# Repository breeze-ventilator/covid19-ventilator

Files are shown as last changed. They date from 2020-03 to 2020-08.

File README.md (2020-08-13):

#  Breeze Ventilator
Welcome to our open-source, low-cost ventilator design! We are a group of students, physicians and engineers who worked on the design to help alleviate the critical need for ventilators during the COVID-19 pandemic.

Here is a [video](https://youtu.be/5ufh_80dSsk) with an overview of our design.

<p align="center">
  <a href="https://youtu.be/5ufh_80dSsk" target="_blank">
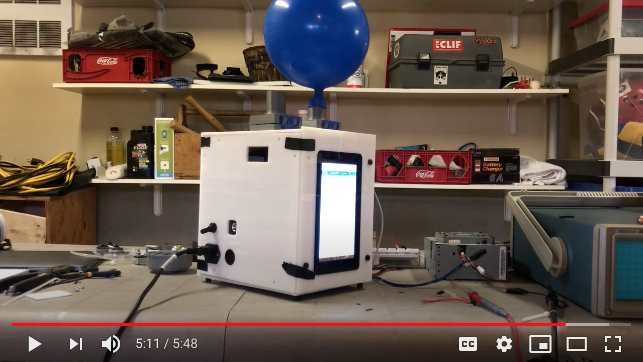
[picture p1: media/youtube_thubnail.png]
Play Introduction Video
    
  </a>
</p>

You can also check out our [in depth design video](https://youtu.be/dRpsoaCI0QA) and [public announcement video](https://youtu.be/4-jjhEgUjkQ).

## Operational Diagram
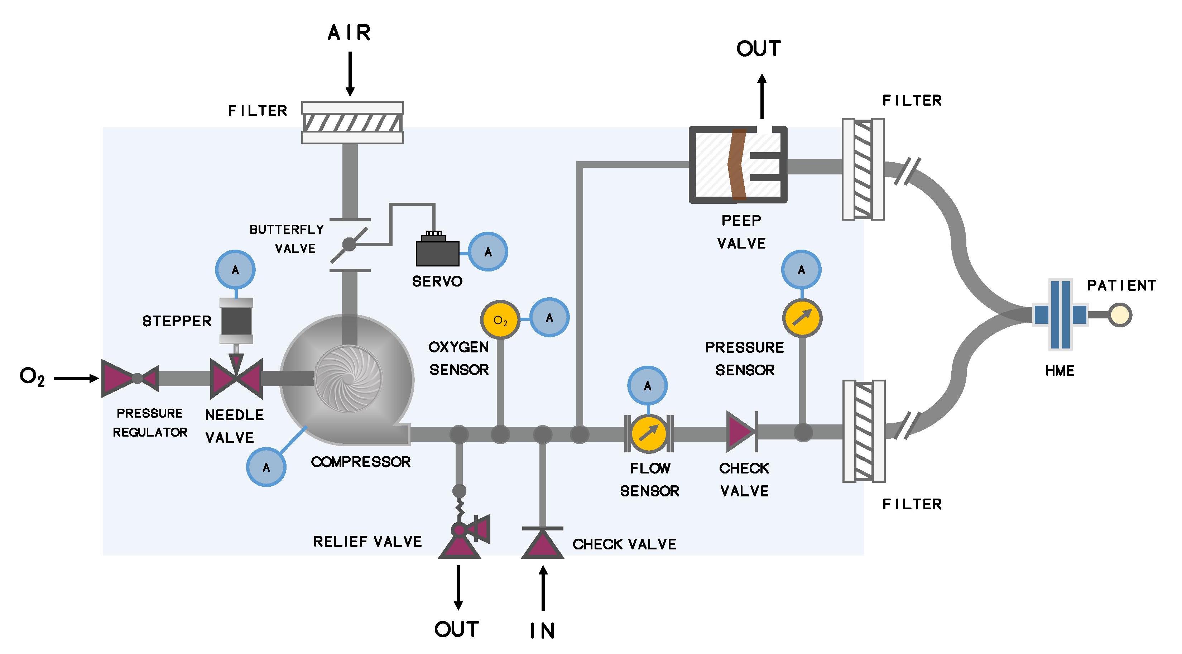
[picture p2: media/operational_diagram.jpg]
operational diagram


## Folder Structure
**Mechanical:** Everything you need to construct the device including the bill of materials and the CAD files.

**Software:** Breeze ventilator code including code for both the interface (running on the Raspberry Pi 4) and the firmware (running on the Arduino Mega).

**Electronics:** PCBs and the circuit diagrams.

**Documentation:** Documentation for operating the device including the User Guide and the Assembly guide, which will help you set-up and run your device smoothly.

## Conclusion

The Breeze Ventilator was built during a design sprint and is not ready to be safely used as a functioning ventilator. Nevertheless, we hope that you will find inspiration from our design and that it will help you with your projects! 

If you have any comments, questions or suggestions you can reach out to our team through raphael.hotter@mail.mcgill.ca

Good luck with your projects and happy creating!

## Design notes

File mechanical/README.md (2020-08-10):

# Mechanical
CADs can be accessed via [the GrabCad repository](https://workbench.grabcad.com/workbench/projects/gcM8LJ5XvqJ3JSgln1WBvlYX60p0lWjT9AxDCpcW93qWFp#/space/gcLw54yDNadcmLN5UvSljD_vmd5pv6YnSIViViylHwmKnL). The GrabCad repository contains all the latest designs and models in individual part format, as sub-assemblies and finally as a master assembly.

For more information on the device's operation as well as some of the functions of individual components, please consult our [documentation](https://github.com/breeze-ventilator/covid19-ventilator/tree/master/documentation).

[Bill of materials](https://docs.google.com/spreadsheets/d/178G98UGMSey0Bp7qwDx1BIGc4RxIQphPiYEJQO0Qzp0/edit?usp=sharing)

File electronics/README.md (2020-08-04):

# Electrical
* `pcb` folder contains KiCad files.
* `parts` folder contains datasheets of off-the-shelf parts.
* `Electrical diagram.pdf` is a simplified diagram of the electronics/
* `Diagram as sent for quote.pdf` is the diagram of the pcb as used.
* `Board Specifications.pdf` contains calculations for the design of the pcb

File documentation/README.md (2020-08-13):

## Documentation 

The Assembly Guide contains detailed instructions on how to assemble the ventilator organized by sub-assembly.
The User Guide illustrates how to properly use and maintain the ventilator.

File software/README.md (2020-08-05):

# Software
The software is composed of the firmware that runs on an Arduino Mega and the interface that runs on a Raspberry Pi 4. The two components communicate via the serial port.

## Firmware for Arduino
The Arduino firmware has several components:
* `Controller` controls the blower fan (`BlowerControl`) using PID, the alarm (`AlarmControl`), the battery charging (`BatteryChargingControl`), the oxygen intake (`OxygenControl`), and the air intake (`AirIntake`)
* `Sensors` reads from the various sensors: `BatteryVoltageSensor` for getting the battery percentage, `FlowSensor` for measuring flow and tidal volume, `PressureSensor`, and `OxygenSensor`
* `PiCommunication` communicates with a Raspberry Pi running the Breeze app over the serial port. Every second, the Arduino sends data to the Pi, and the Pi either replies with new parameters or a standard message indicating that the Pi has not crashed.
* `State` modifies the state of the system based on the parameters, the time, and the sensor data. The state cycles between inhalation and exhalation.
* `Data` saves a short history of the data from the sensors and computes a moving average for the pressure and flow readings.
* `Parameters` contains all the parameters given by the Raspberry Pi. New parameters from the Raspberry Pi get updated upon the start of a new breath.

To run the firmware:
1. Clone the respository `git clone https://github.com/Open-Breeze/covid19-ventilator.git`
2. Open `arduino.ino` in the Arduino IDE
3. Plug in the Arduino Mega to your laptop and press upload.

## Interface
To run the interface for the first time:
1. Clone the respository: `git clone https://github.com/Open-Breeze/covid19-ventilator.git`
2. `cd covid19-ventilator/interface/breeze-electron`
3. `npm install`, which might take a few minutes.
4. `npm run start`

You will also need to have `node` installed, which you can do [here](https://nodejs.org/en/).

A popup error will appear at the start if it hasn't detected the Arduino plugged in or if it can't find `arduino_messager.py`. You can close the error and the rest of the app will remain functional.

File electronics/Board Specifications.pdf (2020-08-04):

### 1 SYSTEM OVERVIEW

To be detailed:
Power supply and p/s fan, main fan, sensors and actuators, fuses, battery connections, switch connections, RPI / Display / sound, backup alarm.

### 2 ELECTRONICS BOARD

### 2.1 PROCESSOR

The on-board processor is an Arduino Mega2560.
P1 through P7, connect to all Arduino connectors except the ICSP header (which is not needed). See schematic for details. It may not be necessary to populate all connector pins, but this may be simplest.

### 2.2 POWER MANAGEMENT

### 2.2.1 Connectors

### 2.2.1.1 Main Power Connector J18

Pin | Name | Function
1 | RECT A POS | + connection to rectifier module
2 | RECT A NEG | GND connection to rectifier module
3 | RECT B POS | + connection to second/redundant rectifier module
4 | RECT B NEG | GND connection to second/redundant rectifier module
5 | INT BAT | + connection to internal battery, fused on board
6 | EXT BAT | + connection to external battery, not fused on board
7 | EXT BAT | + connection to external battery, not fused on board
8 | GND | For batteries or other purposes
9 | GND | For batteries or other purposes
10 | GND | For batteries or other purposes
11 | GND | For batteries or other purposes
12 | GND | For batteries or other purposes
13 | +24V | +24V for alternate ESC supply
14 Spare
15 | BATT-ONOFF-A | Contact closure to enable/disable backup alarm
16 | BATT-ONOFF-B | Contact closure to enable/disable backup alarm

### 2.2.1.2 Raspberry Pi Power Connector U1

USB type A connector, with only power pins connected, to provide +5V from the clean supply. The cable shield is left open.
We can expect a draw of 2A from the Raspberry Pi.

### 2.2.1.3 Buck Converters J19, J20 (bottom side)

4 pins matched to Abra buck converter (+IN, -IN, +OUT, -OUT), 39mm x 16.75 mm rectangle. J19 supplies +5V (clean), J20 supplies +5VP (dirty, for servo)

### 2.2.2 Circuit Protection

The internal battery is fused (F3). A 10A fuse is specified.
External batteries are required to be fused at the battery. The ESC power is fused (F1), current TBD.

### 2.2.3 Sensing

### 2.2.3.1 BATT_CURRENT_SENSE

Function: monitors internal + external battery current. Arduino: pin A6 (P3-7); AREF mode: AVCC
Transfer function:VOUT = (IBATT) (RS) (RL) / 5kΩ + VCC R1 / (R1 + R27) Component values: RS = 10mΩ, R1 = R27 = 100k, RL

= 50k (R1 // R27); VCC = 5V So: VOUT = 0.1Ω • IBATT
From a 10 bit unsigned ADC count, with AREF = AVCC this gives:
IBATT = count * 50A / 1024
Note: on first prototype, the 10mΩ resistor is paralleled with another, so is 5mΩ. Also, only R27 is present, so RL = 100K. Therefore, the above expression is still correct.

### 2.2.3.2 BATT_VOLT_SENSE

Function: monitors (bidirectional) internal + external battery current.
Arduino: pin A7 (P3-8); AREF mode: AVCC
Transfer function: VOUT = (VBATT) R25 / (R24+R25)
Component values: R25 = 10k, R24 = 22k
So: VOUT = VBATT• 0.3125
From a 10 bit unsigned ADC count, with AREF = AVCC this gives:
VBATT = count• 16V / 1024
Reading accuracy is affected by VCC = 5V accuracy. A calibration may be done and stored in EEPROM as a permanent calibration for the unit.

### 2.2.4 Battery Current Control

Function: sets VGS (gate-to-source voltage) of pass transistor Q2, which affects charging (and discharging) current. See 2.2.4.3 and 2.2.4.4 for details.

Arduino: D4 in PWM mode

### 2.2.4.1 Original Transfer Function

VOA = 5V (duty-cycle) (1 + R31 / R30)
If R33 = 0, R32 = DNP: VGS = (V+12V – VOA)
Else, VGS = (V+12V – VOA) (R32 / (R32 + R33))

### 2.2.4.2 Improved Transfer Function

See Error! Reference source not found. for details of the required modification
Transfer function: VGS = 5V (duty-cycle) R32 / R30
Setting R33 = 220Ω, R32 = R30 = 10k: Transfer function: VGS = 5V (duty-cycle)
A slightly higher gain may be desirable, but the transistor should be mostly on with VGS = 5V. Technically the transfer function is also multiplied by the transistor alpha ≈ 1 but this effect should be negligible.

### 2.2.4.3 Charging Control

Q2 VGSaffects the charging current (if mains power is connected) as well as the voltage drop across Q2 in the discharge path. The higher the gate-source voltage, the lower the channel resistance and the more current will flow (at a given VDS).
The improved transfer function is preferred, as it reduces control complexity by removing the dependence on V+12V.
Unfortunately, the exact transfer function of the transistor is unknown, and may vary from unit to unit. Characterization may be required. If the channel resistance RQ2 turns out to be fairly constant over some range of source-to-drain voltage drops, charging current can be roughly predicted as:

ICHARGE = (V+12V. – VBATT) / RQ2

### 2.2.4.4 Mains Power Failure and Discharge Control

Mains power failure may be detected as follows:
- The battery current changes from some positive value to a negative value
- The battery voltage drops from (typically, if fully charged) above 13V to below 12.5V
Note that if Q2 resistance is set relatively high (in a typical trickle charge situation with a full battery), the MOSFET body diode will initially conduct, dropping approx. 0.6V when the power is removed and resulting in V+12V ≈ 12.0V (or a bit lower). When this mains power failure is detected, VGS should be set to the maximum. This will turn on the transistor in low resistance mode, bypassing the body diode and burning less power in the transistor, and transferring more power to the load.

### 2.3 ACTUATOR CONTROLS

### 2.3.1 Servo

The servo interface allows power to be switched on and off, and conveys a PWM signal for pos control.
Arduino: SERVO_OFF D10 (high = off, low = on),

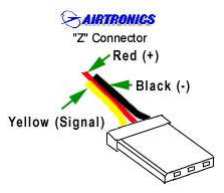
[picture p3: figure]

Runs off “dirty” 5V (on its own buck converter) Servo Connector J5
Pin | Name | Function / Notes
1 GND
2 +5V
3 | PWM control | See ESC data sheet for details See ESC data sheet for details

### 2.3.2 ESC (Speed Control)

12V power on a separate connector
Probably makes sense to fuse this one individually

Ard-PWM9
Note: positive is NC

SERVO_PWM1 D8 (activation level, PWM

, 3A max, 1A continuous.

is one individually.

ition

mode)

ESC Control Connector J3
Pin | Name | Function / Notes
1 GND
2 +5V
3 | PWM control | See ESC data sheet for details See ESC data sheet for details

ESC Power Connector J10
Pin | Name | Function / Notes
1 +5V
2 GND

### 2.3.3 Fan

Power +12V on this connector Tach Ard-D40, with pullup

Fan Connector J14
Pin | Name | Function / Notes
1 GND
2 +5V
3 | Tachometer | Low -going pulses, contact closure (pullup provided)

### 2.3.4 Stepper Motor

Stepper Motor Connector J13
Pin | Name | Function / Notes
1 | OUT1 | TBD
2 | OUT2 | TBD
3 | OUT3 | TBD
4 | OUT4 | TBD

Arduino connections:
IN1: Ard-D45
IN2: Ard-D44
EnA: Ard-PWM2
IN3: Ard-D43
IN4: Ard-D41
EnB: Ard-PWM3

### 2.4 SENSORS

### 2.4.1 Flow Sensor

The flow sensor is a Sensirion SFM3300-D. For details see its data sheet. It connects on J17 as follows. Note that the pinout corresponds to that on the flow sensor itself; allowing easy use of a ribbon cable.
Pin | Name | Function / Notes
1 | Heater power | Mistake – this is 12V but should be +5V. See 2.7.2.
2 | SDA | I2C
3 | GND | For the interface
4 | SCL | I2C
5 | Interface power | +5V or connected to two Arduino pins “FLOWSENSOR_POWER”
6 | GND | For the heater
Connector J17
Arduino I2C pins D20 and D21 are used for I2C communications.
Jumper JP2 allows selection of +5V for the flow sensor power, or Arduino D24 and D22 ganged together. If the Arduino pins are used, the sensor can be power cycled to reset it if communications fail. Take care to switch the pins together, as they are shorted to each other.
O2 Sensor Connector J16
Pin | Name | Function / Notes
1 | Sensor + | Positive voltage developed by sensor with respect to GND (25±2mV)
2 Sensor GND

### 2.4.2 O2 Sensor

The O2 sensor, connected on J16, generates a DC voltage in the approximate range 25mV – 100mV, which is amplified and conveyed to Arduino pin A5.

### 2.4.3 Pressure Sensor

Provision exists for two redundant pressure sensors U2 and U3.
Type Honeywell HSCDLND001PGAA5, output range 0.5V – 4.5V (10% - 90% of VCC). Directly interfaced to Arduino A0 and A1 respectively.

### 2.5 ALARM CIRCUIT

Currently:
Arduino-D26 and D28 (ganged together) energize a relay. Note that care should be taken to set both pins to the same value since they are connected together. The buzzer is connected to the NC contacts, so is kept off. The buzzer is turned on by lowering the pins.
Buzzer on when power off, unless turned off
I really think this has to be redesigned!

### 2.6 OTHER

Flow sensor heater voltage, effect on calibration?

### 2.7 MODIFICATIONS

### 2.7.1 Trace Capacity

Type: board mod, ECO
Reason: +12V trace is not wide enough to adequately carry full current for ESC
Place a wire from the J18-1 or -3 to the ESC fuse (16AWG), on the bottom of the board We may also want to shore up the battery circuit connection.

### 2.7.2 Flow Sensor Connector J17

Type: board mod, ECO
Reason: the flow sensor heater needs 5V, not 12V
Cut the trace to J17-1
Jump from JP2-3 to J17-1

### 2.7.3 O2 Sensor Offset Accuracy, add Voltage Reference

Type: ECO
To be described

### 2.7.4 Decouple AREF

If needed to lower noise.

### 2.7.5 Fix Unconnected R1 pin

Type: board mod, ECO
Connect R1-2 to R27-1.
FIX NOT NEEDED since U8 doesn’t work for negative currents anyway ☹

### 2.7.6 Fix fuse footprint

Type: ECO
The footprint is too short (F1, F3). Various hacks are in place to accommodate a fuse on the v1.0 board.

### 2.7.7 Check and possibly upgrade hex diode package

Type: ECO, board mod if urgent
Diodes D2, D3 probably need a higher peak current rating.

### 2.7.8 Fix RPi USB Connector Pinout

Type: board mod, ECO
Power pins reversed!

### 2.7.9 Add Diode to Alarm Relay Coil

Type: board mod, ECO
From pin 12 to pin 1.

### 2.7.10 Increase Shunt Capacity

Type: board mod, ECO
Shunt should be 5W not 500mW, for the case where the battery has to power the ventilator. On the first prototype, two of them were doubled up (giving, perhaps, a 1 watt capacity).

### 2.7.11 Fix Battery Charge Control

Type: ECO
Measurement is unipolar; it should be bipolar. More generally, we may want to implement a proper charge management circuit. Or, use a current monitor that works bidirectionally.

### 2.7.12 Stepper Driver Heatsink

Type: board mod, ECO
Stepper driver needs a heat sink. The vertical mount one is probably best; this requires a footprint change.

### 2.7.13 ESD Protection on Battery Connection

Type: board mod, ECO
This maybe only really needs to be on the external battery connection (although a full analysis of ESD susceptibility – along with testing – should of course be carried out, and might reveal other paths). On the trace from the external battery to the shunt, a 1uF ceramic capacitor was place (to GND). Additionally, 1k resistors were placed in series with the Arduino analog input pins measuring battery voltage and current.

### 3 ISSUES AND RESOLUTIONS

### 3.1 ELECTRICAL SAFETY FOR BATTERY BACKUP AND BACKUP ALARM

The currently designed circuit, with the main power disconnect also turning off the battery and the backup alarm, may pose electrical safety issues since the switch may not be safety rated between its sets of contacts, particularly not for medical standards.
If this poses a problem, the following scheme will replace it:
The mains switch is replaced by a single pole switch, in series only with the rectifier AC input.
The electronics are designed to power down to the microamp level with a soft on/off switch. The battery circuit is never switched off, thus avoiding the necessity to mix high and low voltage circuits on the same switch. The Arduino is kept powered, even when the system is switched off on battery backup. A primary battery provides backup power to the Arduino, which sounds the backup alarm only if operating power is cut while the ventilator is active.

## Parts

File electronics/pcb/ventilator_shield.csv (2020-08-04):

Source: | C:\Users\Aunt Pancake\Google Drive\03 Ventilator\Breeze\Designs\PCBS\pcb\ventilator_shield.sch
Date: | 4/29/2020 1:06:03 PM
Tool: | Eeschema (5.1.5)-3
Generator: | C:\Program Files\KiCad\bin\scripting\plugins/bom_csv_grouped_by_value_with_fp-custom.py
Component Count: | 74
Line | Ref | Qnty | Value | Cmp name | Footprint | Description | MFN | MPN | VN | VPN | Flag
1 | C1, C2, C3, C4, C5, C6, C7, C10, C11, C12, C13, C14, | 12 | C | C | Capacitor_SMD:C_0805_2012Metric_Pad1.15x1.40mm_HandSolder | Unpolarized capacitor
2 | D1, | 1 | BAV70W | BAV70W | Package_TO_SOT_SMD:SOT-323_SC-70 | Dual 100V 175mA high-speed switching diodes, common cathode, SOT-323
3 | D2, D3, | 2 | BAV756S | BAV756S | Package_TO_SOT_SMD:SOT-363_SC-70-6 | High-speed switching diodes, dual common anode/common cathode, SOT-363
4 | F1, F3, | 2 | Fuse | Fuse | ventilator-parts:LittelFuse_clips_01110501Z_10mm_fuse | Fuse
5 | J1, | 1 | USB_A | USB_A | ventilator-parts:USB_A_TE_Connectivity_292303-1 | USB Type A connector
6 | J2, J7, J8, J10, J16, | 5 | Conn_01x02 | Conn_01x02 | Connector_Molex:Molex_KK-254_AE-6410-02A_1x02_P2.54mm_Vertical | Generic connector, single row, 01x02, script generated (kicad-library-utils/schlib/autogen/connector/)
7 | J3, J5, J14, | 3 | Conn_01x03 | Conn_01x03 | Connector_Molex:Molex_KK-254_AE-6410-03A_1x03_P2.54mm_Vertical | Generic connector, single row, 01x03, script generated (kicad-library-utils/schlib/autogen/connector/)
8 | J13, | 1 | Conn_01x04 | Conn_01x04 | Connector_Molex:Molex_KK-254_AE-6410-04A_1x04_P2.54mm_Vertical | Generic connector, single row, 01x04, script generated (kicad-library-utils/schlib/autogen/connector/)
9 | J17, | 1 | Conn_01x06_Male | Conn_01x06_Male | Connector_PinHeader_2.54mm:PinHeader_1x06_P2.54mm_Vertical | Generic connector, single row, 01x06, script generated (kicad-library-utils/schlib/autogen/connector/)
10 | J18, | 1 | Screw_Terminal_01x16 | Screw_Terminal_01x16 | TerminalBlock_Phoenix:TerminalBlock_Phoenix_PT-1,5-16-3.5-H_1x16_P3.50mm_Horizontal | Generic screw terminal, single row, 01x16, script generated (kicad-library-utils/schlib/autogen/connector/)
11 | J19, J20, | 2 | Conn_01x04 | Conn_01x04 | ventilator-parts:Buck_Converter_Module | Generic connector, single row, 01x04, script generated (kicad-library-utils/schlib/autogen/connector/)
12 | JP1, JP2, | 2 | Jumper_3_Open | Jumper_3_Open | Connector_PinHeader_2.54mm:PinHeader_1x03_P2.54mm_Vertical | Jumper, 3-pole, both open
13 | K1, | 1 | G6S-2 | G6S-2 | Relay_SMD:Relay_DPDT_Omron_G6S-2F | Compact, Industry-Standard 2-pole relay, designed to switch 2A Signal Loads, Single-side Stable
14 | P1, | 1 | Digital | Conn_02x18_Odd_Even | Socket_Arduino_Mega:Socket_Strip_Arduino_2x18 | Generic connector, double row, 02x18, odd/even pin numbering scheme (row 1 odd numbers, row 2 even numbers), script generated (kicad-library-utils/schlib/autogen/connector/) | TE Connectivity AMP Connectors | 4-103321-0 | Digikey Electronics | 4-103321-0
15 | P2, | 1 | Power | Conn_01x08 | Socket_Arduino_Mega:Socket_Strip_Arduino_1x08 | Generic connector, single row, 01x08, script generated (kicad-library-utils/schlib/autogen/connector/) | TE Connectivity AMP Connectors | 4-103321-0 | Digikey Electronics | 4-103321-0
16 | P3, P4, | 2 | Analog | Conn_01x08 | Socket_Arduino_Mega:Socket_Strip_Arduino_1x08 | Generic connector, single row, 01x08, script generated (kicad-library-utils/schlib/autogen/connector/) | TE Connectivity AMP Connectors | 4-103321-0 | Digikey Electronics | 4-103321-0
17 | P5, | 1 | PWM | Conn_01x10 | Socket_Arduino_Mega:Socket_Strip_Arduino_1x10 | Generic connector, single row, 01x10, script generated (kicad-library-utils/schlib/autogen/connector/) | TE Connectivity AMP Connectors | 4-103321-0 | Digikey Electronics | 4-103321-0
18 | P6, | 1 | PWM | Conn_01x08 | Socket_Arduino_Mega:Socket_Strip_Arduino_1x08 | Generic connector, single row, 01x08, script generated (kicad-library-utils/schlib/autogen/connector/) | TE Connectivity AMP Connectors | 4-103321-0 | Digikey Electronics | 4-103321-0
19 | P7, | 1 | Communication | Conn_01x08 | Socket_Arduino_Mega:Socket_Strip_Arduino_1x08 | Generic connector, single row, 01x08, script generated (kicad-library-utils/schlib/autogen/connector/) | TE Connectivity AMP Connectors | 4-103321-0 | Digikey Electronics | 4-103321-0
20 | P10, P11, P13, | 3 | CONN_01X01 | Conn_01x01 | Socket_Arduino_Mega:Arduino_1pin | Generic connector, single row, 01x01, script generated (kicad-library-utils/schlib/autogen/connector/) | None | None | None | None
21 | Q1, Q2, | 2 | SUD19P06-60 | SUD19P06-60 | Package_TO_SOT_SMD:TO-252-2 | 19A Id, 60V Vds, TrenchFET P-Channel Power MOSFET, 60mOhm Ron, 40nC Qg, -55 to 150 °C, TO-252-2
22 | R1, R2, R11, R15, R16, R22, R23, R27, | 8 | R_US | R_US | Resistor_SMD:R_0805_2012Metric_Pad1.15x1.40mm_HandSolder | Resistor, US symbol |  |  | Digikey Electronics
23 | R3, R4, | 2 | 4K7 | R_US | Resistor_SMD:R_0805_2012Metric_Pad1.15x1.40mm_HandSolder | Resistor, US symbol | TE Connectivity Passive Product | CRGCQ0805J4K7 | Digikey Electronics | A130138CT-ND
24 | R12, R26, | 2 | LVK12R010FER | R_Shunt_US | Resistor_SMD:R_Shunt_Ohmite_LVK12 | Shunt resistor, US symbol
25 | R13, | 1 | 1K | R_US | Resistor_SMD:R_0805_2012Metric_Pad1.15x1.40mm_HandSolder | Resistor, US symbol
26 | R24, R28, R29, R31, R33, | 5 | 20K | R_US | Resistor_SMD:R_0805_2012Metric_Pad1.15x1.40mm_HandSolder | Resistor, US symbol | TE Connectivity Passive Product | CRG0805F51K | Digikey Electronics | A126373CT-ND
27 | R25, R30, R32, | 3 | 10K | R_US | Resistor_SMD:R_0805_2012Metric_Pad1.15x1.40mm_HandSolder | Resistor, US symbol | TE Connectivity Passive Product | CRG0805F51K | Digikey Electronics | A126373CT-ND
28 | U1, | 1 | L298HN | L298HN | Package_TO_SOT_THT:TO-220-15_P2.54x2.54mm_StaggerOdd_Lead5.84mm_TabDown | Dual full bridge motor driver, up to 46V, 4A, Multiwatt-15
29 | U2, U3, | 2 | HSCDLND001PGAA5 | HSCDLND001PGAA5 | ventilator-parts:DIP-8_W13.3mm
30 | U4, U10, | 2 | INA138 | INA138 | Package_TO_SOT_SMD:SOT-23-5 | High-Side Measurement Current Shunt Monitor, 36V, SOT-23-5 | Texas Instruments | INA138NA/3K | Digikey Electronics | 296-17936-1-ND
31 | U8, U11, | 2 | OPA188xxDBV | OPA188xxDBV | Package_TO_SOT_SMD:TSOT-23-5 | Zero-Drift, Precision, Low-Noise, Rail-to-Rail Output, 36-V Operational Amplifier, TSOT-23-5

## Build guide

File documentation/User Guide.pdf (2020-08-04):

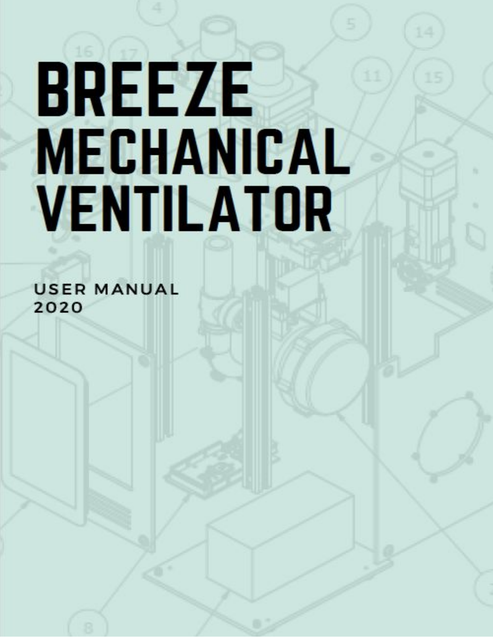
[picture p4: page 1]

I. Medical Note | 2
II. Hardware Operation | 3
a. Providing Power to the Ventilator Unit | 2
b. Turning on the Device | 3
c. Changing the Device’s Filters | 3
d. Connecting Patient Tubes | 4
e. Supplying Oxygen to the Device | 4
f. Cleaning your Device | 4
g. Powering off your Device | 4
III. Software Operation | 5
IV. Setting the Parameters | 6

## I. Medical Note

The ventilator does not include the necessary equipment to measure the patient's oxygen saturation level (saturometer). Monitoring these saturation levels to ensure adequate oxygenation is highly recommended. Use of this ventilator is recommended with a heat and moisture exchanger at the interface between the endotracheal tube and the ventilator tubing.

A closed-system suctioning system proximal to a heat and moisture exchanger (HME) filter will enable clearing of secretions and reduce exposure risk. If resources preclude this, catheter mounts can be used instead.

***DISCLAIMER: BREEZE IS NOT RESPONSIBLE FOR ANY DAMAGES, INJURIES, COMPLICATIONS OR ANY ADVERSE EVENTS THAT OCCUR WITH THE USE OF THE DESIGN/VENTILATOR. IT IS OBLIGATORY THAT A TRAINED MEDICAL PROFESSIONAL OPERATE THE DEVICE. BREEZE AND ITS FOUNDERS ARE FREE FROM ANY AND ALL LIABILITY. It is recommended that individuals follow current Public Health Guidelines and instructions from their respective medical institutions for cleaning their ventilator. The below are suggestions from health care professionals but should not be treated as medical advice. While alarms aim to ensure the patient’s safety and well-being, they cannot be used for absolute safety. Patient safety and mechanical ventilation protocols should be followed.

## II. Hardware Operation

## a. Providing Power to the Ventilator Unit

Table 1. Powering the Unit

i. Mains Supply | Allows the operator to simultaneously (1) power the ventilator unit and (2) charge both the internal and external battery (if connected). No further action is required on the part of the user to initiate battery charging.
ii. External 12V Battery | Allows the operator to power the ventilator using a commercially available 12V battery. To connect the external battery, the operator can use the provided alligator clips which connect directly to the poles of the battery (+Pole/RED Jumper, - Pole/BLACK Jumper). The external battery automatically charges when the ventilator is connected to the mains supply. The charging status and battery life are displayed on the user interface.
Iii. Internal 12V Battery | A 12V rechargeable battery which is sufficient to operate the system independently for a short duration (ex. switching operations, power outages). It should not be used for long-term operation as the 1-3 hour window depends on operational demands. The internal battery is housed within the ventilator, can be accessed via partial disassembly of the unit, and charges automatically when the system is connected to a mains source. Both charging status and battery life are displayed on the user-interface.

## b. Turning on the Device

In order to power on the ventilator unit, first (1) activate the alarm switch which should make an audible alarm followed by the (2) main power switch which will turn off the alarm. If you do not hear the alarm do not use the device. Both switches are located on the front-panel of the ventilator and identified with labels. The ventilator display is automatically activated when connected to one of the three power sources described in section I.a.

## c. Changing the Device’s Filters

The filter housings are located on the top panel of the ventilator unit. To change the existing filters, the operator can lift the blue latches on the filter housing assembly, remove the soiled ones and replace with HEPA filters. An additional air intake filter is mounted to the side panel. The air intake filter can be pressed into the body of the unit.

## d. Connecting Patient Tubes

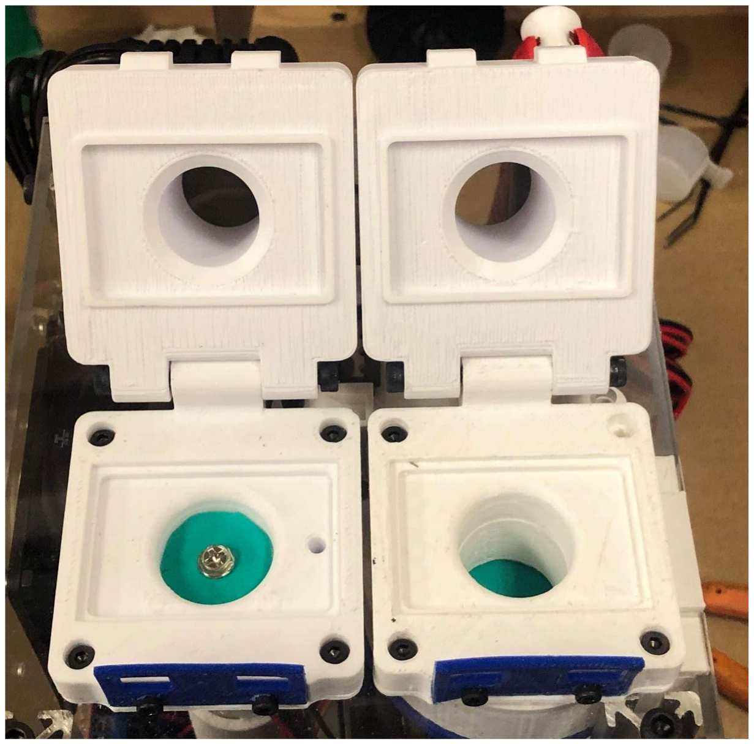
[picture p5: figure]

The patient y-tube consisting of standard medical corrugated tubing fitted with 22 mm universal adapters easily slots into the filter housings.

## e. Supplying Oxygen to the Device

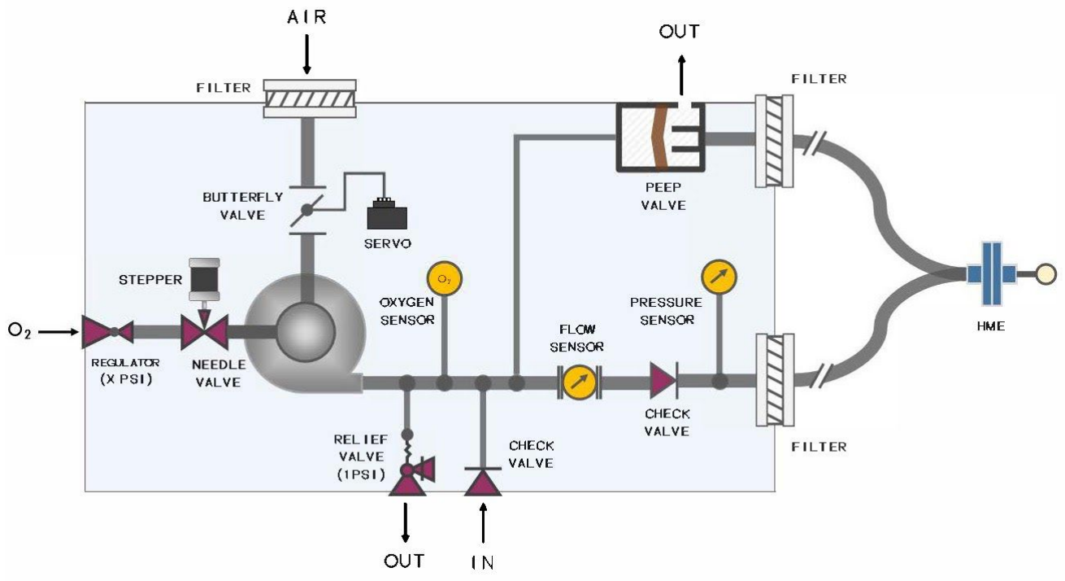
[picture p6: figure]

The ventilator unit contains an adapter enabling the attachment of a pressurized oxygen line. The oxygen source can be a pressurized tank or any other source of pressurized medical oxygen. The maximum oxygen line pressure that can safely be delivered to this ventilator is 200 psi. For the ambient air supply, no additional action is required.

## f. Cleaning your Device

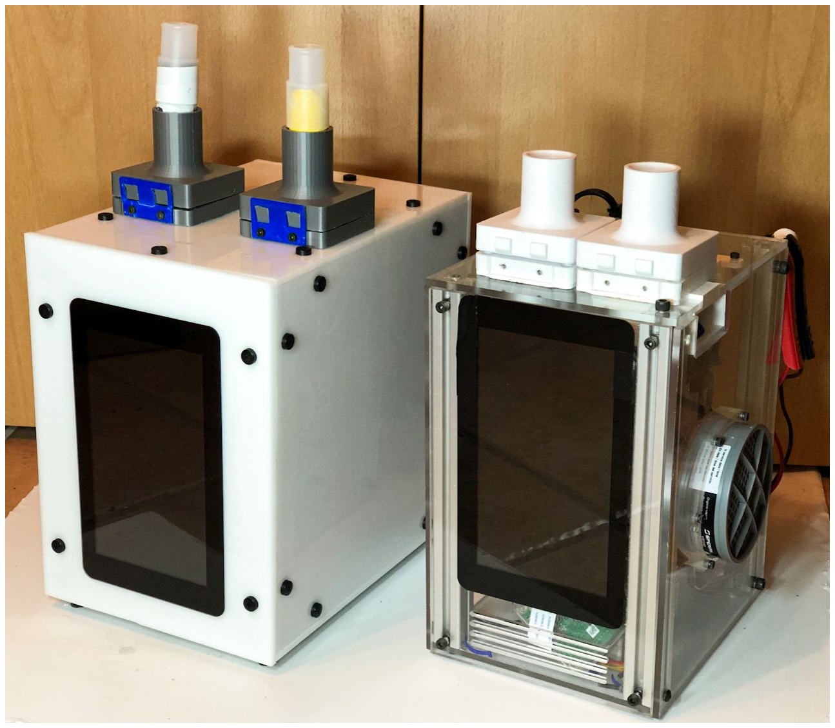
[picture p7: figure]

All exposed surfaces can be disinfected. The ventilator surface can withstand all standard medical-grade hospital ventilator disinfectants.
- The external and internal surfaces include the tablet, 3D printed parts, acrylic casing and all wires.
- The filter housings can be detached from the body of the ventilator and either disinfected or printed again.
- The air intake filter can be replaced between patients.
- The tubing circuit should be handled as usual.
- For added risk mitigation, the PEEP valve may be disinfected with any standard medical disinfectants.

## g. Powering off your Device

To power off the device, first disable the main power, then the alarm switch. It is not necessary to unplug the device from the mains source or to disconnect the internal/external batteries.

## III. Software Operation

After the ventilator has booted up, a helpful setup screen appears, with an option to run automated validation tests.

### Setup Screens

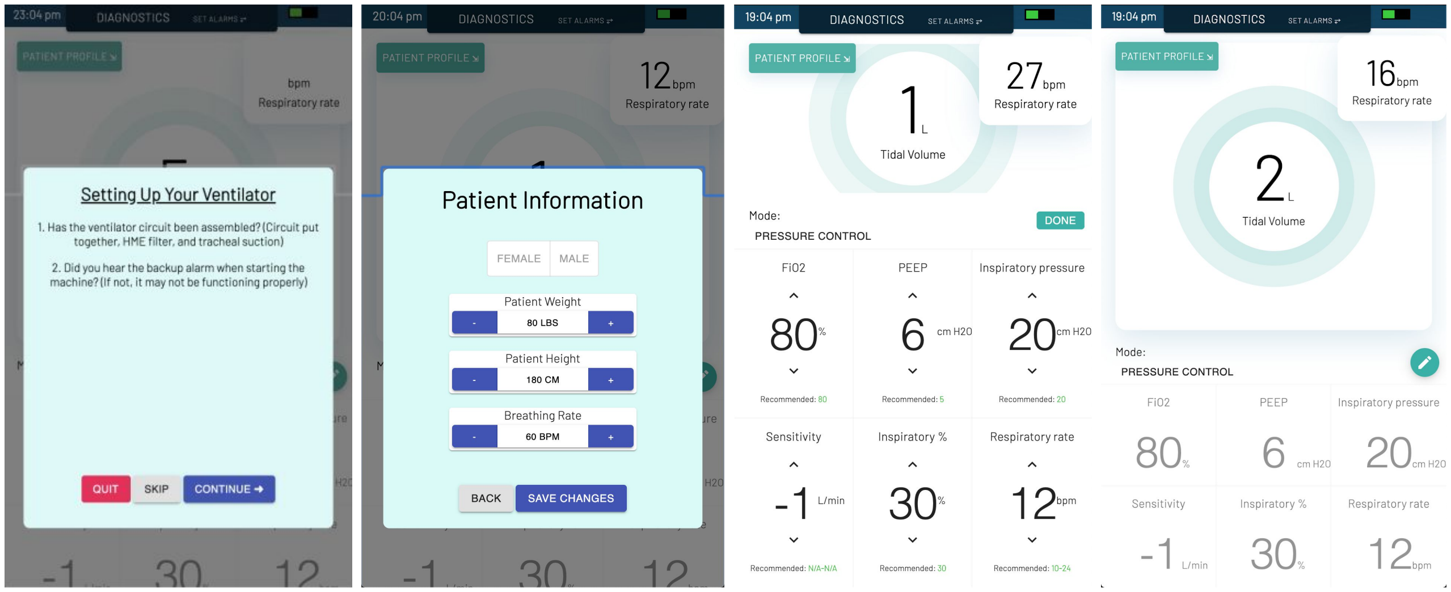
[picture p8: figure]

Table 2. The Interface

i. Parameters Screen | Recommendations for how to set each parameter are integrated in the software. (See section below for details on setting up the screen)
ii. Alarms Screen | Alarm thresholds must be set. A history of the alarms that have sounded in the last 24 hours are available on the display.
iii. Observation Screen | Two values are displayed at all times to facilitate monitoring the patient’s condition: tidal volume and pressure. A standby mode ceases flow in the ventilator system to minimize exposure to viral particles when changing filters.

## IV. Setting the Parameters

Prior to the ventilatory settings, you will be asked to enter the patient’s measurements.

Table 3. Breath Parameters

i. Pressure Control and Pressure Support | At the top of the parameters setting screen, two initial settings allow you to choose between Pressure Control and Pressure Support. The chosen mode depends on the patients’ respiratory rate and spontaneous breaths as Pressure Control breaths have a fixed time cycle and Pressure Support breaths are flow-cycled.
ii. Respiratory Rate | The respiratory rate (for Pressure Control mode only) reflects the number of breaths a patient will receive in a minute.
iii. Fi02 | Fi02 represents the fraction of inspired oxygen, i.e. the proportion of the inspired gas delivered to the patient that is composed of oxygen.
iv. PEEP | The PEEP is the positive end-expiratory pressure, the amount of pressure left in the ventilated lungs at the end of expiration.
v. Sensitivity | This sensitivity represents the inspiratory flow which signals to the ventilator that the patient is initiating a breath. This ventilator’s detection threshold value is set to 1L/min and does not require operator setting.
vi. Inspiratory Pressure | This pressure will support the patient’s work of breathing.
vii. Inspiratory time or Inspiratory:Expiratory (I:E) Ratio | This value is only pertinent in pressure control mode. It represents the time spent inspiring relative to the total time of the breath (inspiration+expiration together).

Table 4. Alarms

i. High minute ventilation | The high minute ventilation alarm sounds when the volume of air entering and exiting the patient’s lung is above a threshold value. This alarm often indicates a high respiratory rate or an increase in patient demand for air caused by pain or anxiety.
ii. Low minute ventilation | The low minute ventilation alarm sounds when the volume of air entering and exiting the patient’s lungs are below a threshold value.
iii. High Pressure | This alarm detects high pressure in the circuit and can be triggered by secretions, coughing, bronchospasm, or obstructed tubin.
iv. Low Expiratory Pressure | Low pressure alarms reflect a sudden drop in ventilator circuit pressure and are usually associated with leaks or disconnections.

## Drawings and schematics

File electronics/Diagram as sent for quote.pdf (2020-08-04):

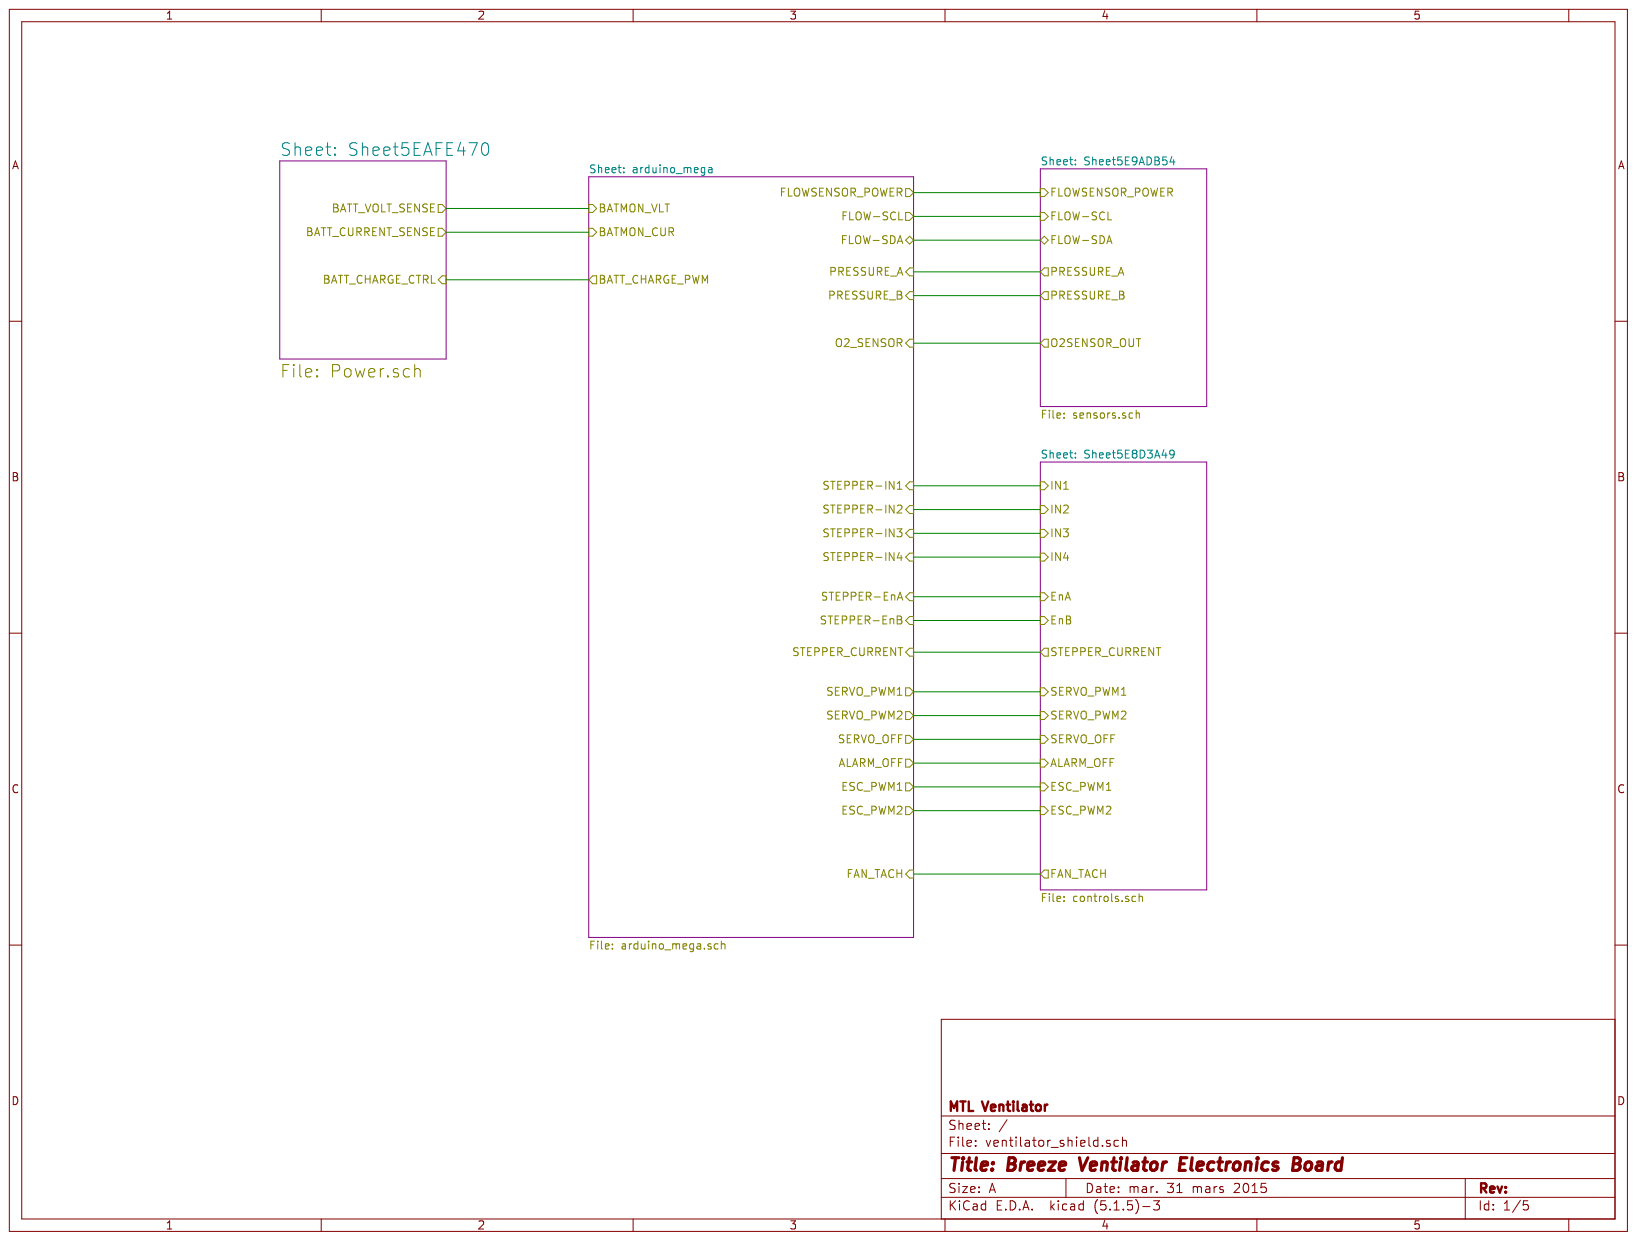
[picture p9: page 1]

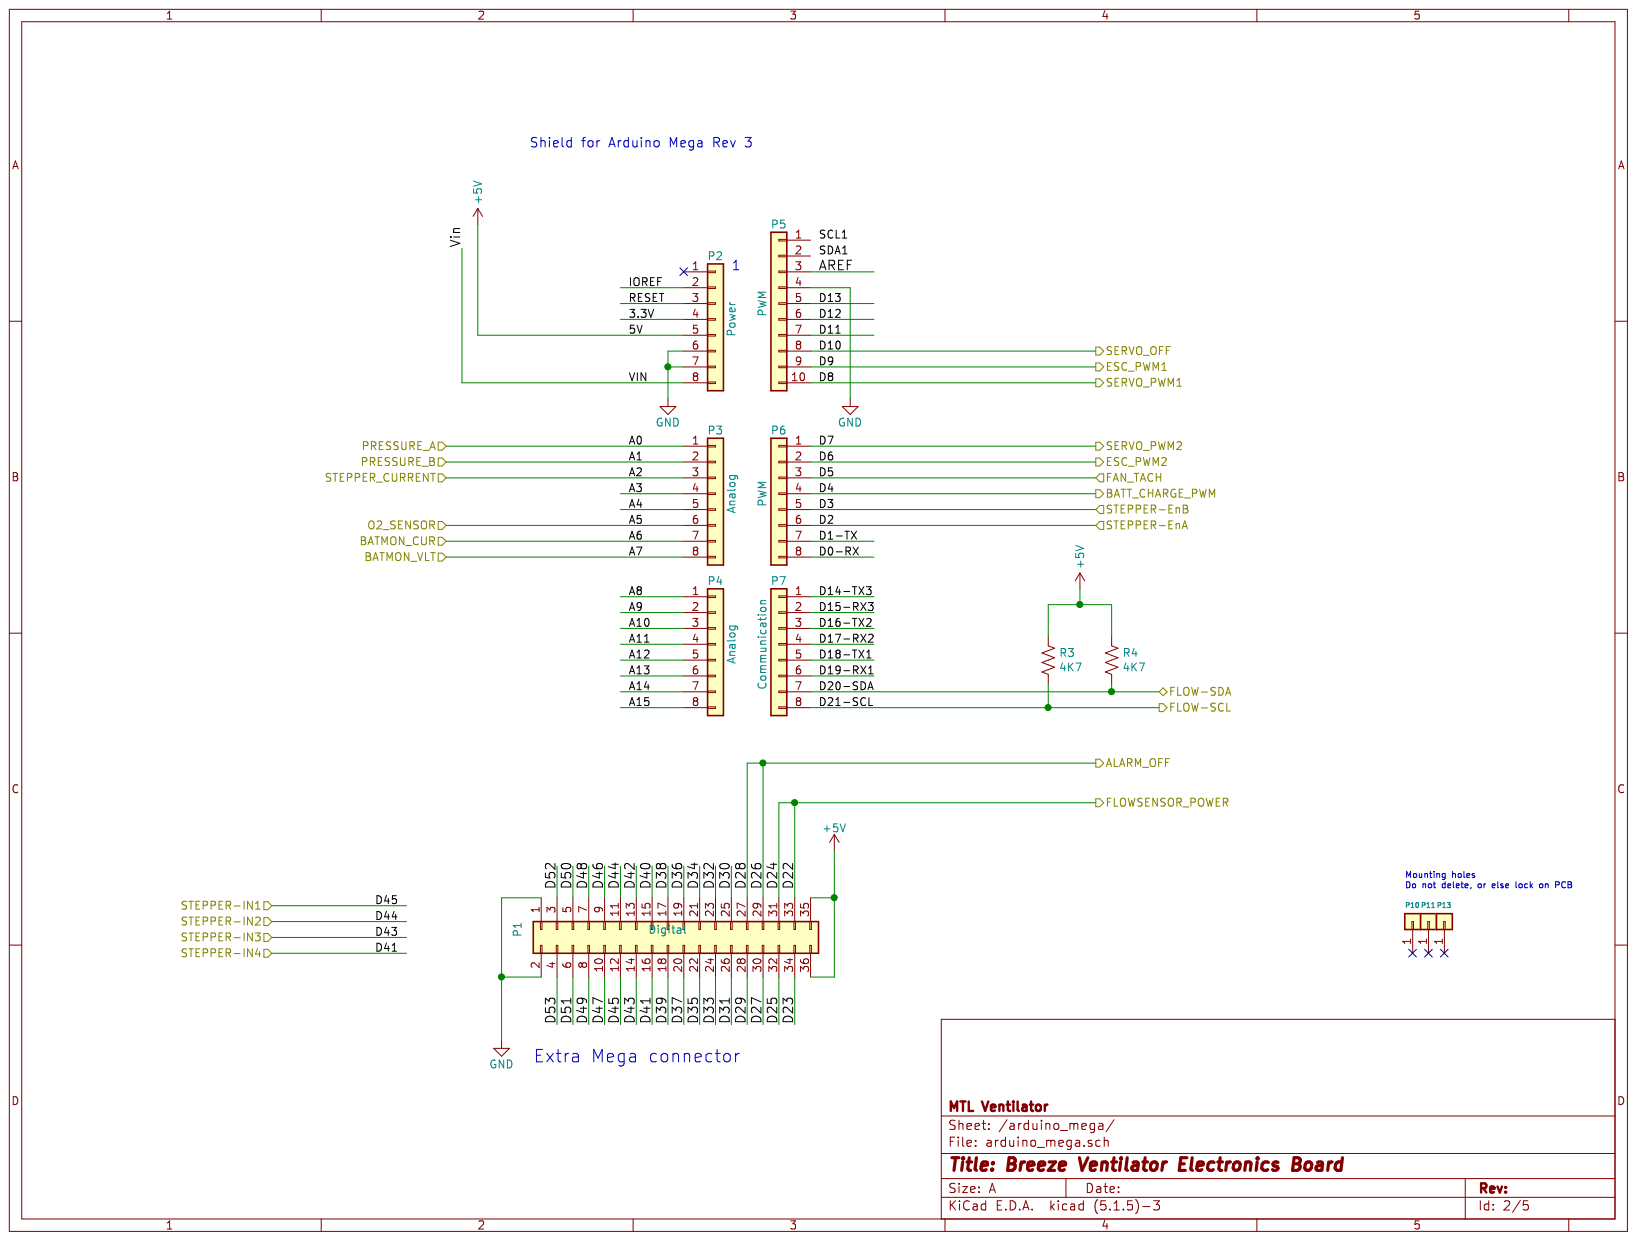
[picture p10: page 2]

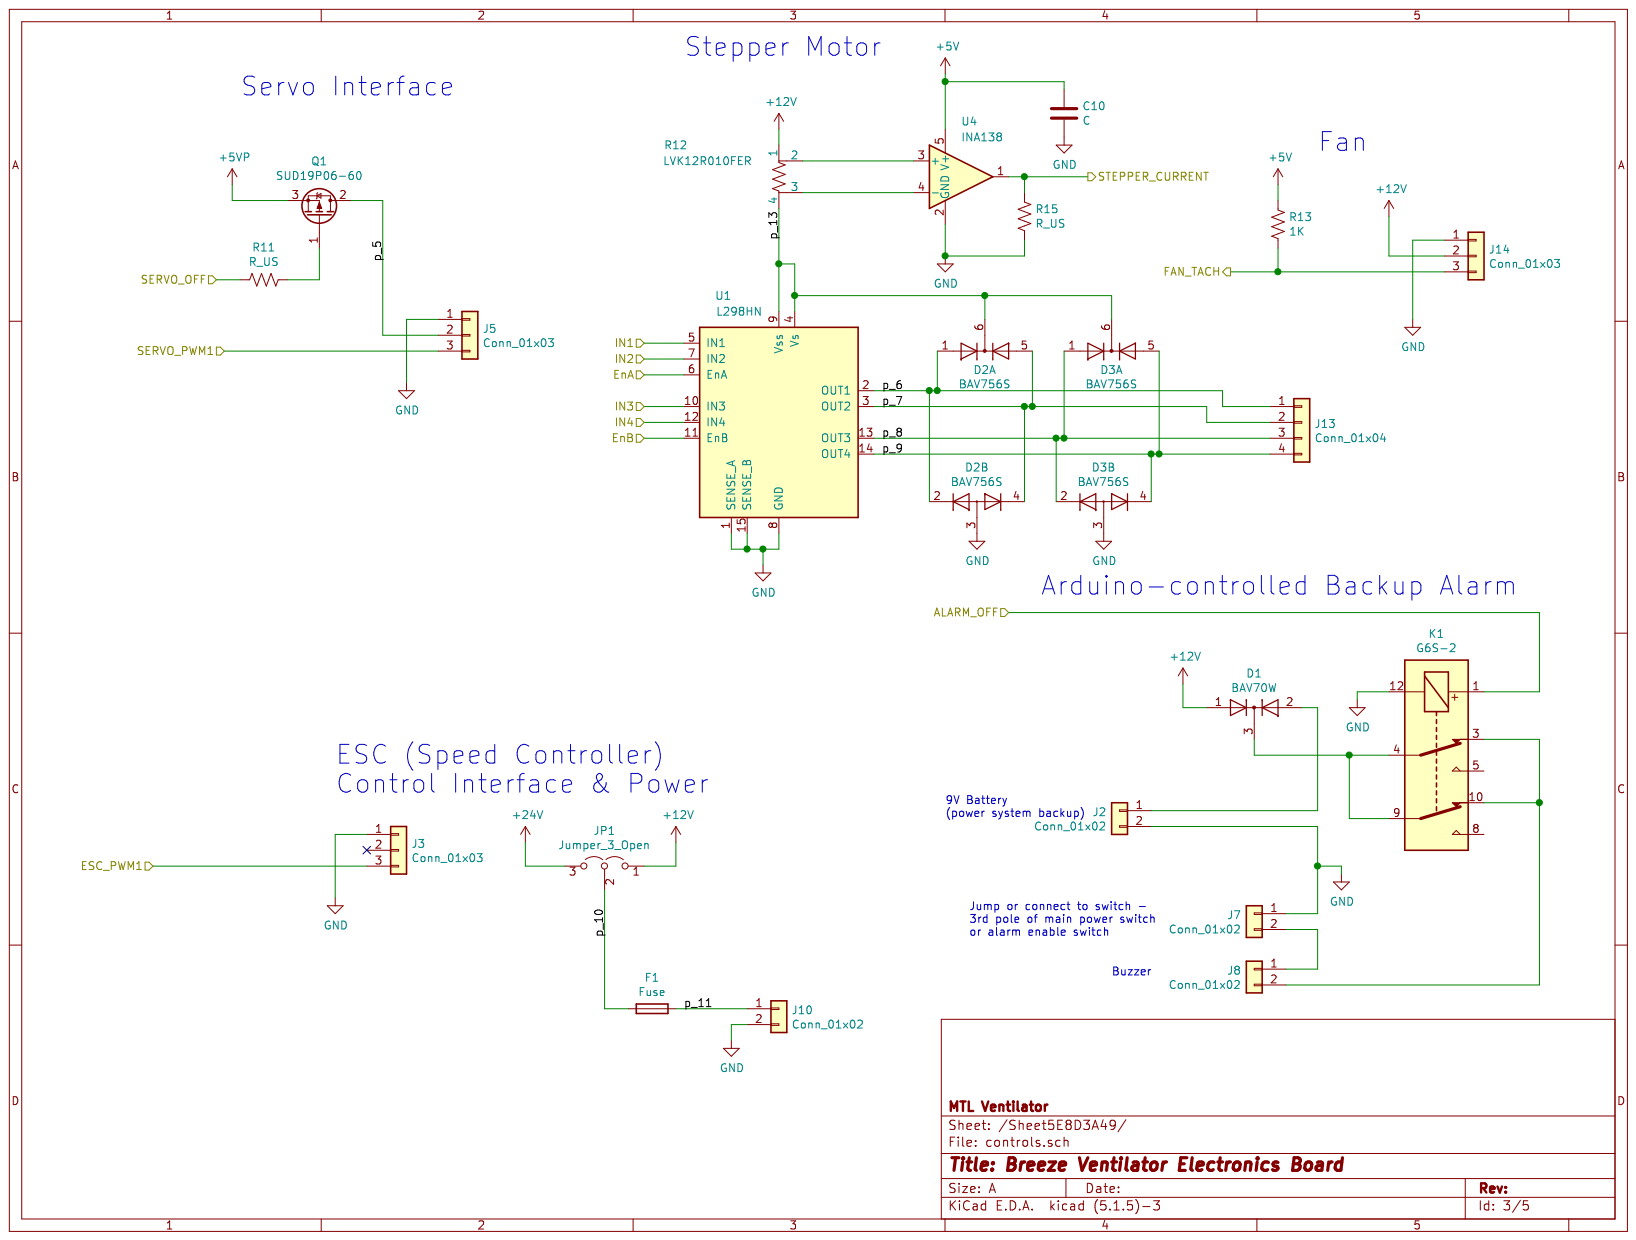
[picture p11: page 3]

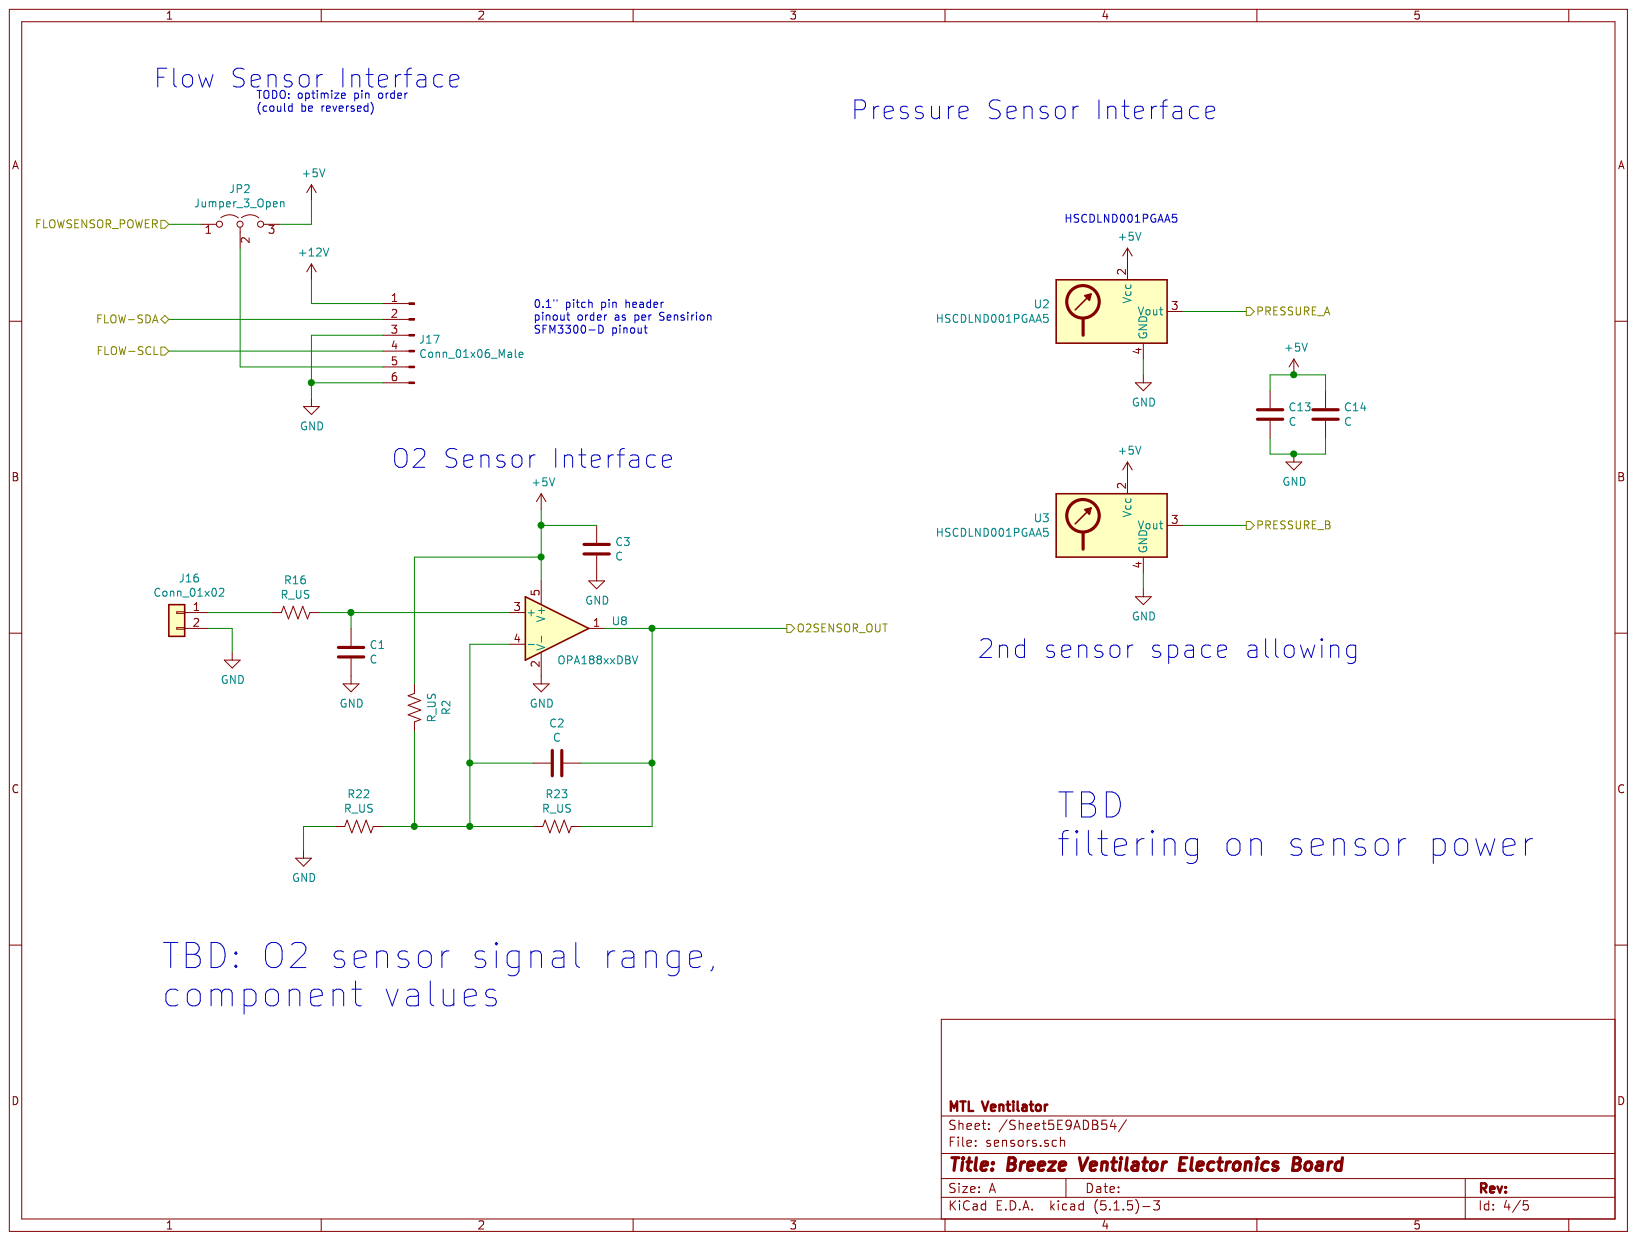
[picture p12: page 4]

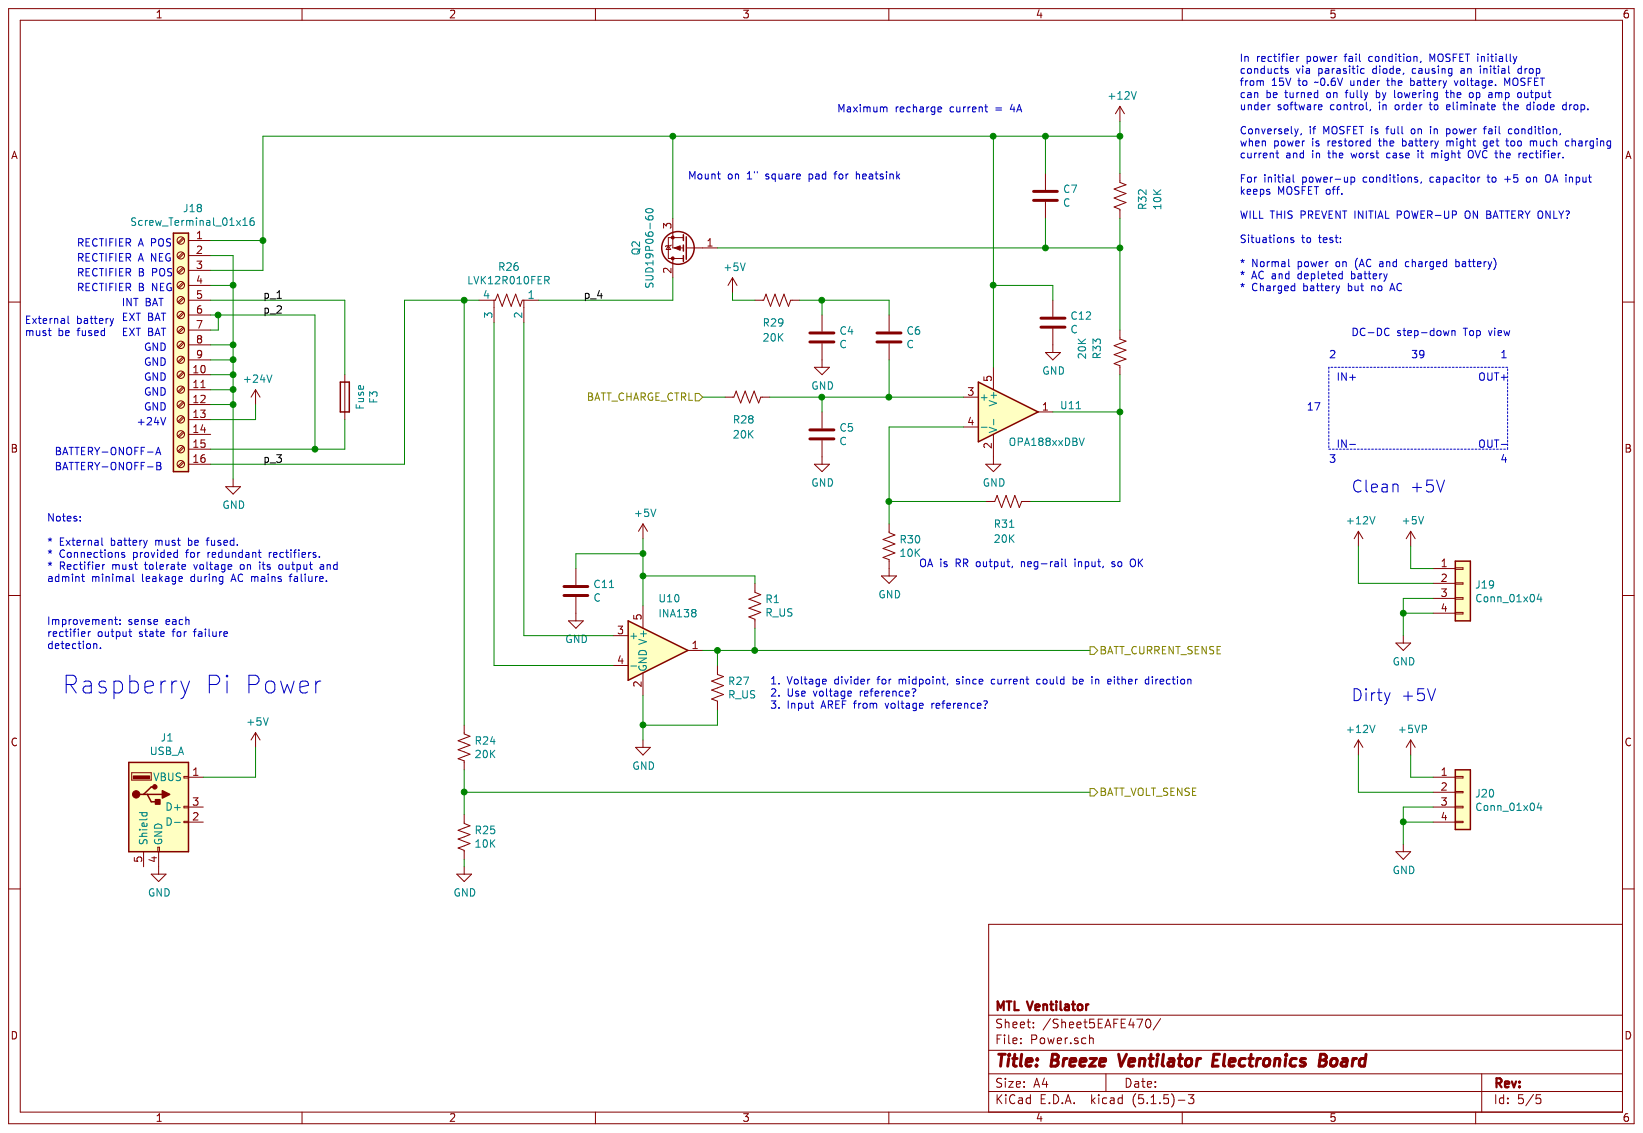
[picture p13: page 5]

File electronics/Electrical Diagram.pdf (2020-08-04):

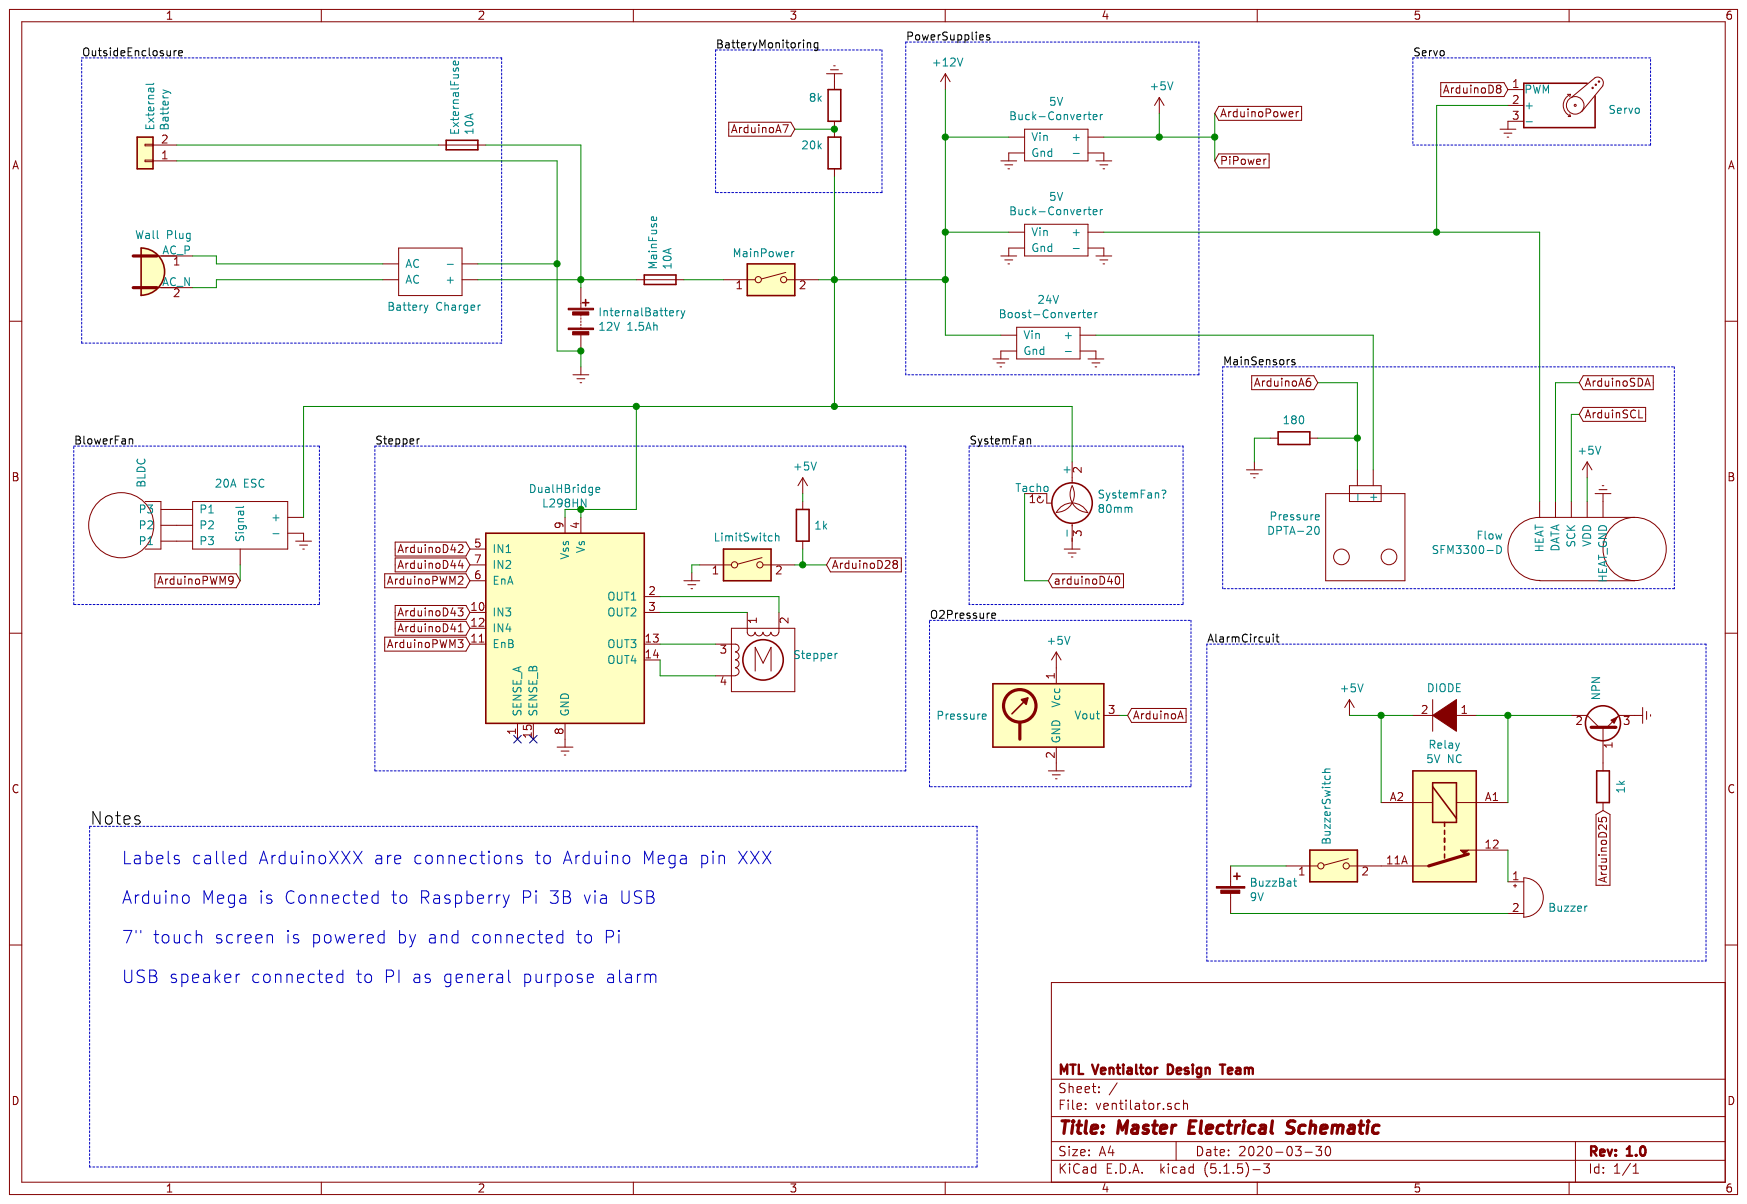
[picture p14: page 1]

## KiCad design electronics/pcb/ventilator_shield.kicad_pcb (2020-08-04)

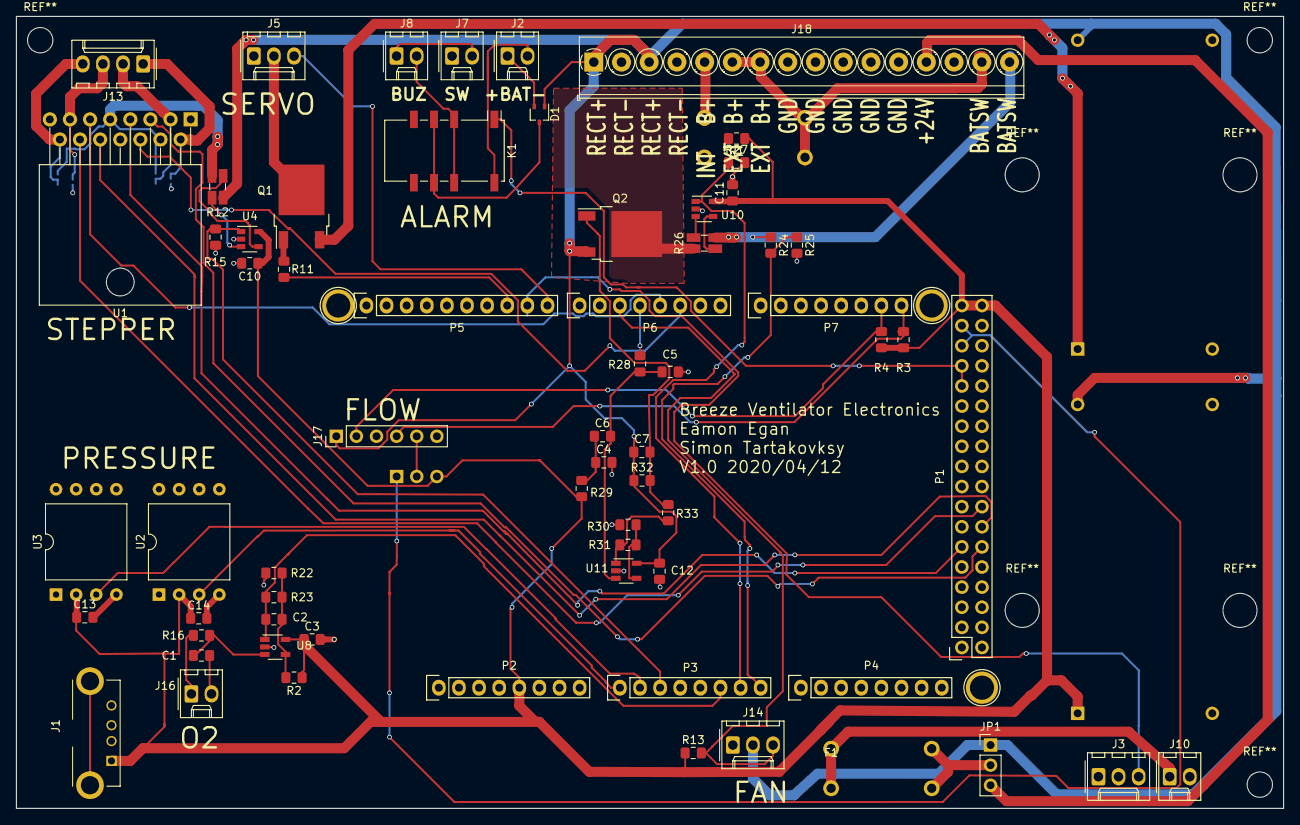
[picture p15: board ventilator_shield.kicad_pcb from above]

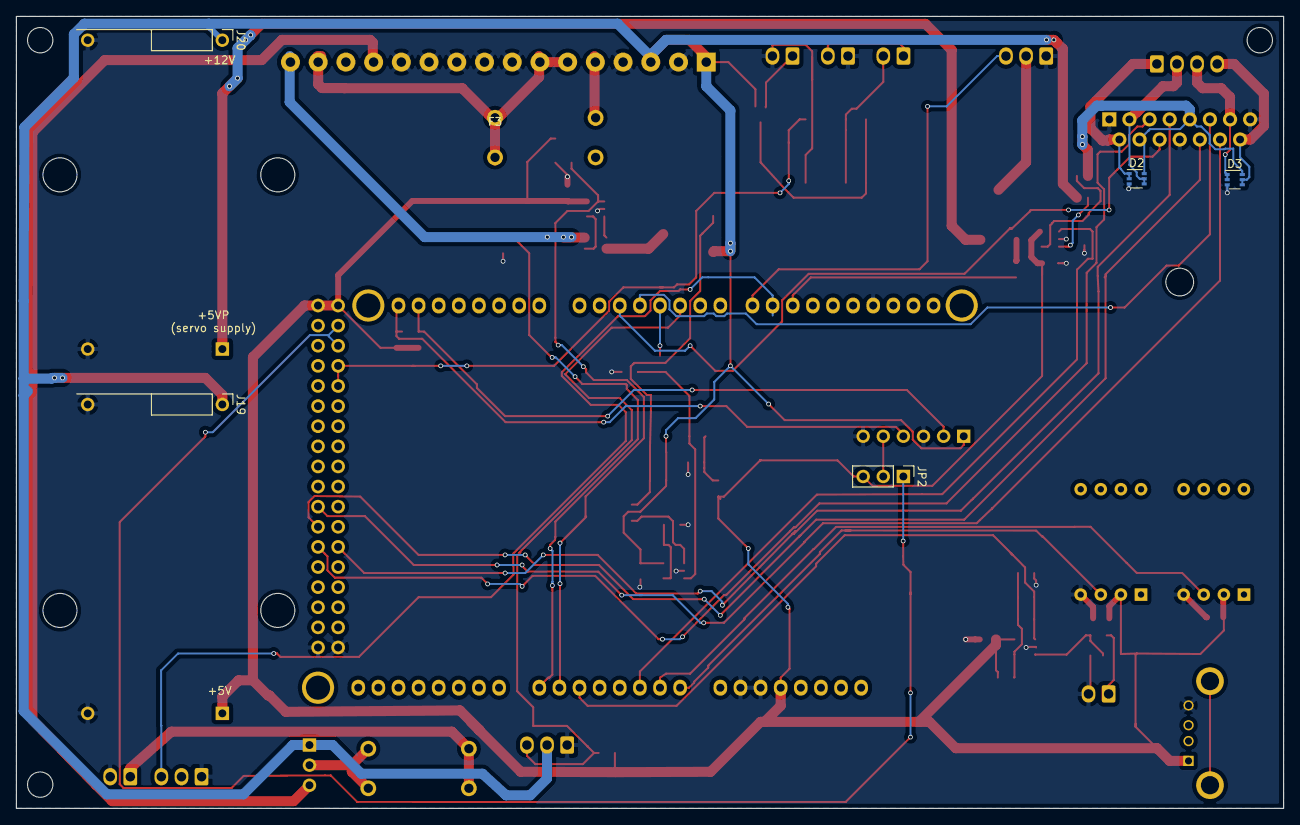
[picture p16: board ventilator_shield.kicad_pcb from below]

Board: 2 copper layers, 160.0 x 100.0 mm, 74 parts (6 on the bottom side), 56 nets.

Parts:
C1, C2, C3, C4, C5, C6, C7, C10, C11, C12, C13, C14: C; C_0805_2012Metric_Pad1.15x1.40mm_HandSolder
D1: BAV70W; SOT-323_SC-70
D2, D3: BAV756S; SOT-363_SC-70-6
F1, F3: Fuse; LittelFuse_clips_01110501Z_10mm_fuse
J1: USB_A; USB_A_TE_Connectivity_292303-1
J2, J7, J8, J10, J16: Conn_01x02; Molex_KK-254_AE-6410-02A_1x02_P2.54mm_Vertical
J3, J5, J14: Conn_01x03; Molex_KK-254_AE-6410-03A_1x03_P2.54mm_Vertical
J13: Conn_01x04; Molex_KK-254_AE-6410-04A_1x04_P2.54mm_Vertical
J17: Conn_01x06_Male; PinHeader_1x06_P2.54mm_Vertical
J18: Screw_Terminal_01x16; TerminalBlock_Phoenix_PT-1,5-16-3.5-H_1x16_P3.50mm_Horizont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
J19, J20: Conn_01x04; Buck_Converter_Module
JP1, JP2: Jumper_3_Open; PinHeader_1x03_P2.54mm_Vertical
K1: G6S-2; Relay_DPDT_Omron_G6S-2F
P1: Digital; Socket_Strip_Arduino_2x18
P2: Power; Socket_Strip_Arduino_1x08
P3, P4: Analog; Socket_Strip_Arduino_1x08
P5: PWM; Socket_Strip_Arduino_1x10
P6: PWM; Socket_Strip_Arduino_1x08
P7: Communication; Socket_Strip_Arduino_1x08
P10, P11, P13: CONN_01X01; Arduino_1pin
Q1, Q2: SUD19P06-60; TO-252-2
R1, R2, R11, R15, R16, R22, R23, R27: R_US; R_0805_2012Metric_Pad1.15x1.40mm_HandSolder
R3, R4: 4K7; R_0805_2012Metric_Pad1.15x1.40mm_HandSolder
R12, R26: LVK12R010FER; R_Shunt_Ohmite_LVK12
R13: 1K; R_0805_2012Metric_Pad1.15x1.40mm_HandSolder
R24, R28, R29, R31, R33: 20K; R_0805_2012Metric_Pad1.15x1.40mm_HandSolder
R25, R30, R32: 10K; R_0805_2012Metric_Pad1.15x1.40mm_HandSolder
U1: L298HN; TO-220-15_P2.54x2.54mm_StaggerOdd_Lead5.84mm_TabDown
U2, U3: HSCDLND001PGAA5; DIP-8_W13.3mm
U4, U10: INA138; SOT-23-5
U8, U11: OPA188xxDBV; TSOT-23-5

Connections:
+5V: C3.1, C10.1, C11.1, C13.1, C14.1, J1.1, J19.1, JP2.3, P1.35, P1.36, P2.5, R1.1, R2.1, R3.1, R4.1, R13.1, R29.2, U2.2, U3.2, U4.5, U8.5, U10.5
+5VP: J20.1, Q1.3
+12V: C7.1, C12.1, D1.1, J14.2, J17.1, J18.1, J18.3, J19.2, J20.2, JP1.1, Q2.3, R12.1, R32.1, U11.5
+24V: J18.13, JP1.3
/Sheet5E8D3A49/ALARM_OFF: K1.1, P1.27, P1.29
/Sheet5E8D3A49/ESC_PWM1: J3.3, P5.9
/Sheet5E8D3A49/EnA: P6.6, U1.6
/Sheet5E8D3A49/EnB: P6.5, U1.11
/Sheet5E8D3A49/FAN_TACH: J14.3, P6.3, R13.2
/Sheet5E8D3A49/IN1: P1.12, U1.5
/Sheet5E8D3A49/IN2: P1.11, U1.7
/Sheet5E8D3A49/IN3: P1.14, U1.10
/Sheet5E8D3A49/IN4: P1.16, U1.12
/Sheet5E8D3A49/SERVO_OFF: P5.8, R11.2
/Sheet5E8D3A49/SERVO_PWM1: J5.3, P5.10
/Sheet5E8D3A49/STEPPER_CURRENT: P3.3, R15.1, U4.1
/Sheet5E8D3A49/p_5: J5.2, Q1.2
/Sheet5E8D3A49/p_6: D2.1, D2.2, J13.1, U1.2
/Sheet5E8D3A49/p_7: D2.4, D2.5, J13.2, U1.3
/Sheet5E8D3A49/p_8: D3.1, D3.2, J13.3, U1.13
/Sheet5E8D3A49/p_9: D3.4, D3.5, J13.4, U1.14
/Sheet5E8D3A49/p_10: F1.2, JP1.2
/Sheet5E8D3A49/p_11: F1.1, J10.1
/Sheet5E8D3A49/p_13: D2.6, D3.6, R12.4, U1.4, U1.9
/Sheet5E9ADB54/FLOW-SCL: J17.4, P7.8, R3.2
/Sheet5E9ADB54/FLOW-SDA: J17.2, P7.7, R4.2
/Sheet5E9ADB54/FLOWSENSOR_POWER: JP2.1, P1.31, P1.33
/Sheet5E9ADB54/O2SENSOR_OUT: C2.1, P3.6, R23.1, U8.1
/Sheet5E9ADB54/PRESSURE_A: P3.1, U2.3
/Sheet5E9ADB54/PRESSURE_B: P3.2, U3.3
/Sheet5EAFE470/BATT_CHARGE_CTRL: P6.4, R28.2
/Sheet5EAFE470/p_1: F3.2, J18.5
/Sheet5EAFE470/p_2: F3.1, J18.6, J18.7, J18.15
/Sheet5EAFE470/p_3: J18.16, R24.1, R26.4
/Sheet5EAFE470/p_4: Q2.2, R26.1
/arduino_mega/BATMON_CUR: P3.7, R1.2, R27.1, U10.1
/arduino_mega/BATMON_VLT: P3.8, R24.2, R25.1
GND: C1.2, C3.2, C4.2, C5.2, C10.2, C11.2, C12.2, C13.2, C14.2, D2.3, D3.3, J1.4, J2.2, J3.1, J5.1, J7.1, J10.2, J14.1, J16.2, J17.3, J17.6, J18.2, J18.4, J18.8, J18.9, J18.10, J18.11, J18.12, J19.3, J19.4, J20.3, J20.4, K1.12, P1.1, P1.2, P2.6, P2.7, P5.4, R15.2, R22.2, R25.2, R27.2, R30.2, U1.1, U1.8, U1.15, U2.4, U3.4, U4.2, U8.2, U10.2, U11.2
unnamed: C1.1, R16.1, U8.3
unnamed: C2.2, R2.2, R22.1, R23.2, U8.4
unnamed: C4.1, C6.1, R29.1
unnamed: C5.1, C6.2, R28.1, U11.3
unnamed: C7.2, Q2.1, R32.2, R33.2
unnamed: D1.2, J2.1
unnamed: D1.3, K1.4, K1.9
unnamed: J7.2, J8.1
unnamed: J8.2, K1.3, K1.10
unnamed: J16.1, R16.2
unnamed: J17.5, JP2.2
unnamed: Q1.1, R11.1
unnamed: R12.2, U4.3
unnamed: R12.3, U4.4
unnamed: R26.2, U10.3
unnamed: R26.3, U10.4
unnamed: R30.1, R31.2, U11.4
unnamed: R31.1, R33.1, U11.1

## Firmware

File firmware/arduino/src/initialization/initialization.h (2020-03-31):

#ifndef INIT_H
#define INIT_H

// TODO: Simon are these valid?

//=========== Global PARAMS  ===============//
// Define reading rates (ms)
#define FLOW_READ_RATE 100
#define PRESSURE_READ_RATE 2  // 500 Hz freq => 2 ms period

// Defines size of global storage arrays
#define NUM_OF_PRESSURE_MEASUREMENTS 10 
#define NUM_OF_FLOW_MEASUREMENTS 10 

#define SEND_DATA_TIMEOUT 10

// https://www.arduino.cc/reference/en/language/functions/analog-io/analogread/

// Input pin numbers
#define PRESSURE_PIN 6
#define BATTERY_PIN 7
#define FAN_SENSOR_PIN 40
#define STEP_MOTOR_ZERO_PIN A5

// Output pin 
#define BLOWER_PIN 9 //is pwm (servo)
#define ALARM_PIN 25
#define AIR_CONTROL_PIN 8 //is pwm (servo)

// O2 stepper motor, needs 4 pins
#define O2_CONTROL_PIN0 42
#define O2_CONTROL_PIN1 44
#define O2_CONTROL_PIN2 43
#define O2_CONTROL_PIN3 41

#define O2_ENABLE1_PIN 2
#define O2_ENABLE2_PIN 3

#define FLOW_COEFFICIENT 1

#define HOME_SWITCH_PIN 28

// Stepper and Servo initialization
#define O2_STEPPER_SPEED 60 // rpm (TODO: Arbitrary value)

#define STEPPER_INITIALIZATION_TIMEOUT 360 // Assuming there are 360 steps in a rotation, one full rotation = timed out (TODO: Arbitrary value)

// https://www.arduino.cc/en/Reference/ServoWrite
#define BLOW_FAN_INITIAL_POSITION 15  // 0 = min, 180 = max, 90 = midpoint (TODO: this is currently arbitrary)
#define AIR_INTAKE_INITIAL_POSITION 110 // 0 = min, 180 = max, 90 = midpoint (TODO: arbitraty)

#define TIMEOUT_ERROR -1

#define FLOW_READING_FREQUENCY 500 // 500 Hz
#define MAIN_PRESSURE_READING_FREQUENCY 500
#define OXYGEN_PRESSURE_READING_FREQUENCY 100
#define BATTERY_VOLTAGE_READING_FREQUENCY 1

// Pi Comms
#define BAUD_RATE 9600
#define TIME_BETWEEN_PI_SENDING 100
#define MAX_SERIAL_CONNECTION_WAIT_TIME 1000
#define PI_MAX_WAIT_TIME 1000000
#define PI_PING_INTERVAL 100

#endif

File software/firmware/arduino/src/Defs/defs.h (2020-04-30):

#ifndef INIT_H
#define INIT_H

#define PARAMETER_BYTE_LENGTH 13

// Utilities
#define SECONDS_TO_MILLISECONDS 1000
#define MINUTES_TO_MILLISECONDS 60000
#define CENTIMETERS_TO_MILIMETERS 10
#define TENTH_OF_SECOND_TO_MILISECONDS 100

// Modes and breathing stages
#define OFF_MODE 0
#define PRESSURE_CONTROL_MODE 1
#define PRESSURE_SUPPORT_MODE 2
#define INHALATION_STAGE 3
#define EXHALATION_STAGE 4
#define OFF_STAGE 5

// Input pin numbers
#define ALARM_PIN 25
#define AIR_CONTROL_PIN 8 //is pwm (servo)

// Stepper and Servo initialization
#define O2_STEPPER_SPEED 60 // rpm (TODO: Arbitrary value)

// https://www.arduino.cc/en/Reference/ServoWrite
#define AIR_INTAKE_INITIAL_POSITION 110 // 0 = min, 180 = max, 90 = midpoint (TODO: arbitraty)

#define FLOW_READING_FREQUENCY 500 // Hz
#define MAIN_PRESSURE_READING_FREQUENCY 500
#define OXYGEN_READING_FREQUENCY 20
#define BATTERY_VOLTAGE_READING_FREQUENCY 5

// Pi Comms
#define BAUD_RATE 9600
#define PI_PING_INTERVAL 100
#define TIME_BETWEEN_DATA_SENDING_TO_PI 1000

// Pressure support
#define MIN_INHALATION_TIME_PRESSURE_SUPPORT 400

#endif

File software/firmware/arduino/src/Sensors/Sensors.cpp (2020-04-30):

#include "Sensors.h"

Sensors::Sensors(int flowReadingFrequency,
                 int mainPressureReadingFrequency,
                 int oxygenReadingFrequency,
                 int batteryVoltageReadingFrequency)
    : flowSensor(FLOW_IC2_ADDRESS, FLOW_OFFSET, FLOW_SCALE),
    mainPressureSensor(MAIN_PRESSURE_PIN),
    oxygenSensor(OXYGEN_SENSOR_PIN)
    // batteryVoltageSensor(BATTERY_VOLTAGE_PIN)
  {
  _timeBetweenFlowReadings = 1.0/flowReadingFrequency * SECONDS_TO_MILLISECONDS;
  _timeBetweenMainPressureReadings = 1.0/mainPressureReadingFrequency * SECONDS_TO_MILLISECONDS;
  _timeBetweenOxygenReadings = 1.0/oxygenReadingFrequency * SECONDS_TO_MILLISECONDS;
  _timeBetweenBatteryPercentageReadings = 1.0/batteryVoltageReadingFrequency * SECONDS_TO_MILLISECONDS;
  _timeBetweenPrints = 100;

  _lastFlowReadTime = 0;
  _lastMainPressureReadTime = 0;
  _lastOxygenReadTime = 0;
  _lastBatteryPercentageReadTime = 0;
  _lastPrintTime = 0;
}

void Sensors::init() {
  flowSensor.init();
}

void Sensors::readSensorsIfAvailableAndSaveSensorData(Data &data, State &state) {
  // take sensor readings
  if (isTimeToReadFlow()) {
    int error = 0;
    // flow read in L/min
    float flowValue = flowSensor.read(&error); // we're not doing anything with this error yet
    if (flowValue > 250) { // max range
      flowValue = 0;
    }

    // flow in L/min, tidal volume in L
    float delta_time = (float)(millis() - _lastFlowReadTime);
    delta_time /= MINUTES_TO_MILLISECONDS;
    data.saveFlowReading(flowValue);

    if (state.breathingStage == INHALATION_STAGE) {
      data.updateTidalVolume(flowValue, delta_time);
    }
    // Serial.println(flowValue);
    _lastFlowReadTime = millis();
  }
  if (isTimeToReadOxygen()) {
    float oxygenReading = oxygenSensor.read();
    data.saveOxygenReading(oxygenReading);
    _lastOxygenReadTime = millis();
  }
  if (isTimeToReadMainPressure()) {
    float pressureValue = mainPressureSensor.read(); // analog read (difference between this pressure and atmospheric pressure)
    data.saveMainPressureReading(pressureValue);
    _lastMainPressureReadTime = millis();
    // if (isTimeToPrint()) {
    //   Serial.println(data.getMainPressureAverageForPID());
    //   _lastPrintTime = millis();
    // }
  }
  // if (isTimeToReadBatteryPercentage()) {
  //   unsigned int batteryPercentage = batteryVoltageSensor.readPercentage();
  //   data.saveBatteryPercentage(batteryPercentage);
  //   // Serial.println(batteryPercentage);
  //   _lastBatteryPercentageReadTime = millis();
  // }
}

int Sensors::isTimeToReadFlow() {
  return isTime(_lastFlowReadTime, _timeBetweenFlowReadings);
}
int Sensors::isTimeToReadMainPressure() {
  return isTime(_lastMainPressureReadTime, _timeBetweenMainPressureReadings);
}
int Sensors::isTimeToReadOxygen() {
  return isTime(_lastOxygenReadTime, _timeBetweenOxygenReadings);
}
int Sensors::isTimeToReadBatteryPercentage() {
  return isTime(_lastBatteryPercentageReadTime, _timeBetweenBatteryPercentageReadings);
}
int Sensors::isTimeToPrint() {
  return isTime(_lastPrintTime, _timeBetweenPrints);
}

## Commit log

2020-03-25 new folder structure: adding arduino code to same github repo
2020-03-25 creation of superficial arduino code
    jsut a sketch
2020-03-28 Initial arduino code commit
2020-03-29 Arduino code changes
2020-03-29 restructuring of arduino
2020-03-29 arduino progress and refactoring
2020-03-30 Foundation layed out for sockets
2020-03-30 SocketListeners Ready
2020-03-30 Added sample data streaming to diagnostics and colour
2020-03-31 added battery
2020-03-31 BATTERY GO DOWN
2020-04-08 Initial Electron App
    We now have our initial electron app! Rendering, routing both seem to be
    working. Next up is connecting to socket + arduino messaging and
    confirming that works!
2020-04-08 Electron Uses Top Now
    We now talk via arduino + client messagers via electron.
2020-04-09 Remove Settings + Setup Pages
    We will reintroduce a setup flow in the future but the current one was
    super janky and it's a lot easier to just delete it.
2020-04-12 All primary firmware components have been completed (#33)
    * testing without arduino done
    * set default parameters
    * testing
    * a
    * test3
    * a
    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
2020-04-12 Fixed onboarding screen UI and added power off button.
2020-04-12 Removed power off button from PatientProfile.jsx
2020-04-12 handle new parameters to arduino
2020-04-12 socket change
2020-04-12 socket round 3
2020-04-12 socket round 4
2020-04-12 socket round 5
2020-04-12 socket v7
2020-04-12 socket v8
2020-04-13 arduino messager changes
2020-04-14 Added sample data listener
2020-04-14 Sample listener changes
2020-04-15 Added the patient profile button back in Please enter the commit message for your changes. Lines starting
2020-04-15 flow triggering works (#58)
2020-04-15 pressure support working
2020-04-15 changed flow frequency reading to 500
2020-04-15 added power/standby button
2020-04-15 Revert "added power/standby button" (#62)
2020-04-15 patient profile button change
2020-04-15 pressure sensor
2020-04-15 uncommented picomms + changed pressure to float
2020-04-15 oxygen sensor
2020-04-16 added python dependencies, called arduino file
2020-04-16 socketio bug fix
2020-04-28 Firmware update: (#84)
    * test 2
    * lowered Kp to 3
    * test 3
    * test
    * printing set pressure
    * b
    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
2020-04-29 workaround for pressure, change defaults and messages
2020-04-29 re-insert test data sampler
2020-04-29 re-insert sounds
2020-04-30 firmware update: added header file for oxygen stepper
2020-04-30 firmware update: air valve (#90)
2020-04-30 firmware update: battery control + allow higher output on blower
2020-04-30 firmware: send min & max pressure to pi for alarms (#85)
2020-08-04 added pcbs
    [Power.sch, arduino_mega.sch, controls.sch, sensors.sch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]
2020-08-04 cleaned electronics
    [ventilator_shield.csv]
2020-08-04 cleaning or smthing
    [Power.sch, arduino_mega.sch, controls.sch, sensors.sch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]
